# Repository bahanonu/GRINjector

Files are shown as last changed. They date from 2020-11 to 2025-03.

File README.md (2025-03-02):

# GRINjector

<!-- ![image](https://user-images.githubusercontent.com/5241605/97932336-945bbb80-1d24-11eb-9098-b09245b89beb.png) -->
<!-- ![image](https://user-images.githubusercontent.com/5241605/98111332-4a262780-1e55-11eb-887c-673c79a5a353.png) -->

<!-- <img src="https://user-images.githubusercontent.com/5241605/124192957-f23ecf80-da7a-11eb-9894-70a6294c9538.png" width="42%" align="right" alt="ciatah_logo"> -->






__GRINjector__ is a device for injecting gradient-refractive index (GRIN) lens probes into animals. The advantages are:
1. The injection needle displaces brain tissue, improving targetting and minimizing tissue compression.
2. The GRIN is held in place during retraction of the placement needle from the GRIN and the GRINJector device.
3. The guide needle can be easily swapped for other guide needles depending on the diameter and length of the GRIN lens probe.

This repository contains CAD files for printing GRINjector version 3.0 components and assembling them into a usable GRINjector. 

The assembly and use of the GRINjector is also detailed in our book chapter.
* GRINjection section: https://link.springer.com/protocol/10.1007/978-1-0716-2039-7_13#Sec6.
* Fig. 3: https://link.springer.com/protocol/10.1007/978-1-0716-2039-7_13/figures/3.

For those conducting calcium imaging experiments and analysis, we have a software package called CIAtah: https://github.com/bahanonu/ciatah.

Questions? Contact: Biafra Ahanonu (github [at] bahanonu [dot] com).

## Components

The below figure illustrates several of the main components:



Below is a list of components needed to assemble a GRINjector:
* Vernier micrometer. SM-13. Newport.
* Bearing stage. 9066-COM. Newport.
* 4x lock screws that come with 9066-COM.
* Model 1770, Kopf Instruments. For attaching GRINjector to stereotaxic arm.
* GRINjector bottom connector (`grinjector_bottom_connector`)
* GRINjector main needle connector top (`grinjector_mainneedle_connector_top`)
* GRINjector main needle connector bottom (`grinjector_mainneedle_connector_bottom`)
* Stereotaxic holder attachment (`stereotaxic_holder_attachment`)
* 2x - 8-32 x 1'' cap screw.
* 1x - 4-40 x 3/16'' cap screw.
* 1x - 4-40 x 1/4'' cap screw.
* 4x - 4-40 x 5/16'' cap screw.
* Luer lock needle (`Holder needle`) matched to the size of the GRIN lens probe.
  * For 1-mm GRIN lens probe, recommend 17G needle that is 0.04-0.042'' inner diameter (e.g. https://www.mcmaster.com/6710A24/).
    * Rubber tubing: https://www.mcmaster.com/5236K203/.
  * For 0.5-mm GRIN lens probe, recommend 21G needle (e.g. https://www.mcmaster.com/6710A28/).
* Thin needle (`Stability needle`) that is ~80-mm long and between 0.25-0.5-mm diameter (smaller version for smaller GRIN lens probes).
  * 0.25-mm diameter: https://www.mcmaster.com/6710A48/.
  * 0.5-mm diameter: https://www.mcmaster.com/6710A28/.
  * Used to hold the GRIN probe in place as outer sheath is removed. For the above pieces, may need to cut the metal piece from the Luer lock portion.

## Printing

The main parts are provided as STEP and STL files to allow printing on nearly all commonly used 3D printers (Straysys, uPrint, ). We recommend printing with a high-resolution printer to ensure optimal fit and one with easy to remove support material—we have used VeroBlackPlus on a Stratasys Objet30 and found that to work quite well.

## Assembly

Below are step-by-step by step instructions for assembling the GRINjector after building the necessary parts.

1. Connect the SM-13 and 9066-COM to form a functional setup. Remove the locking plate from 9066-COM as below (see https://www.newport.com/medias/sys_master/images/images/he5/h5b/9366526427166/906806B-9066-9067-User-Manual.pdf).



2. Using 8-32 cap screws, connect the `Stereotaxic holder attachment` to the back of the 9066-COM, connecting to the top-most holes near the micrometer.



3. Next, pull down the bearing stage so that the two 4-40 holes in the back are exposed, place 4-40 x 5/16'' cap screws in each hole.



4. Tap the `grinjector_mainneedle_connector_bottom` holes with a 4-40 tap then place it onto `9066-COM` as below and screw in the 4-40 x 5/16'' cap screws (red below).



5. Align the `lock screws` that comes with `9066-COM` to each of the four holes on each side of the `grinjector_bottom_connector`.



6. Next, place a blunt or syringe tip `Holder needle` that matches the size of your GRIN lens probe into the groove of the `grinjector_mainneedle_connector_bottom` piece then place the `grinjector_mainneedle_connector_top` piece on top. Screw the `grinjector_mainneedle_connector_top` in place with 4-40 x 5/16'' cap screws then secure the `Holder needle` with a 4-40 x 1/4'' cap screw.

  * Syringe tip Luer-lock needles allow easier parting of the underlying tissue as the GRINjector is lowered into the brain or spinal cord tissue.



7. Next, obtain a long, `Stability needle` (e.g. ~80-mm long, 0.5-mm diameter) and thread through the small opening at the top of `grinjector_bottom_connector`. The `Stability needle` will then go through the `Holder needle`. Lock the needle in place with a 4-40 x 3/16'' cap screw.

  * Note that the end of the `Stability needle` can be sanded or polished to avoid the chance that it will scratch the GRIN lens probe during implantation and retraction.



8. Lastly, verify that the chosen `Holder needle` fits the GRIN lens probe tightly and that you can push the GRIN lens probe out of the `Holder needle` smoothly by twisting the SM-13 micrometer.
  
  * Note: rubber tubing (e.g. for 1-mm diameter probes, https://www.mcmaster.com/5236K203/) can be placed at the end of the `Holder needle` to ensure the GRIN lens does not slip from the GRINjector during use while still allowing the `Holder needle` to be retracted from around the GRIN.



You are now done assembled the GRINjector! Happy imaging.



## Animal experiments

To use the GRINjector in an animal:
* Attach the GRINjector onto a stereotaxic arm then perform your normal GRIN lens probe crainotomy surgery.
* Lower the GRIN into the brain using the GRINjector (below diagram, left).
* After placement at desired coordinates in tissue, raise the blunt tip needle by twisting the micrometer until the needle is clear of the GRIN lens probe. The red needle secures the GRIN in place during retraction of the device.
* Secure the GRIN in place with dental cement, UV glue, or your adhesive of choice then after it as set, slowly raise the GRINjector using the stereotaxic arm.
* If your stereotaxic arm allows angles, the GRINjector can be used to target the same site at different angles to avoid vasculature or vital brain regions (below diagram, right).



## Head bar

We use several different headbar designs that allow us to clamp the animal during baseplate mounting, attaching the miniature microscope before experiments, and other uses. An example head bar design can be found in `cad_files/DXF`.



## Notes

`Holder needle`:
* SAI Infusion works well: https://www.sai-infusion.com/products/blunt-needles?variant=333055723. The plastic has some give that works well with the 3D printed parts.
* Check that the needle inner diameter is as close to the GRIN lens size as possible, e.g. for 1-mm that would be 17G needles that are ~0.04-0.042'' (https://www.mcmaster.com/6710A24/). 
* Sometimes users have to check a couple needles within the same batch since there will be slight size variations that will optimally fit their GRIN lenses.

`Stability needle`:
* We have found that a metal needle (e.g. could go with https://www.mcmaster.com/6710A48/ or similar then cut the needle to the desired length) does not cause significant scratching.
* If you have a grinder (handheld or bench), polisher (e.g. https://www.ultratecusa.com/product/ultrapol-end-edge-polisher/), or similar surface, then you can make the needle surface smoother and flat. 
* Alternatively can place a small drop of optical glue on the end of the needle and cure it or look for plastic needles.

## Acknowledgements

I would like to thank [Prof. Benjamin Grewe](https://www.ini.uzh.ch/en/institute/people?uname=bgrewe) for helping inspire and provide feedback on the initial GRINjector design.

## References

Please cite the [Ahanonu and Corder, 2022](https://doi.org/10.1007/978-1-0716-2039-7_13) book chapter if you used procedures detailed here.

```bibtex
@incollection{ahanonu2022recording,
  title={Recording Pain-Related Brain Activity in Behaving Animals Using Calcium Imaging and Miniature Microscopes},
  author={Ahanonu, Biafra and Corder, Gregory},
  booktitle={Contemporary Approaches to the Study of Pain},
  pages={217--276},
  year={2022},
  publisher={Springer}
}
```

Alternatively, please cite our publication [Corder*, Ahanonu*, et al. _Science_ 2019](http://science.sciencemag.org/content/363/6424/276.full) :

```Latex
@article{corderahanonu2019amygdalar,
  title={An amygdalar neural ensemble that encodes the unpleasantness of pain},
  author={Corder, Gregory and Ahanonu, Biafra and Grewe, Benjamin F and Wang, Dong and Schnitzer, Mark J and Scherrer, Gr{\'e}gory},
  journal={Science},
  volume={363},
  number={6424},
  pages={276--281},
  year={2019},
  publisher={American Association for the Advancement of Science}
}
```

## License

Copyright (C) 2015-2025 Biafra Ahanonu

This project is licensed under the terms of the MIT license. See LICENSE file for details.

## Repository stats
- Hits (starting 2020.11.02)
-  (starting 2020.11.02)

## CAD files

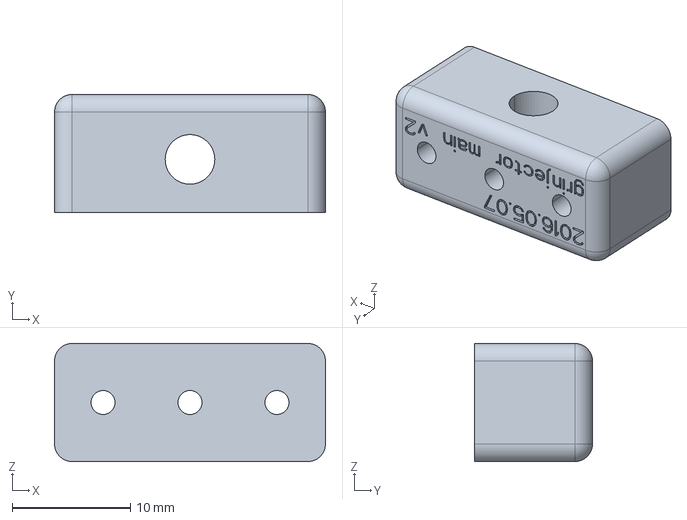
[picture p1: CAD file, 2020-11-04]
cad_files/STEP/grinjector_mainneedle_connector.stp
22.9 x 10.0 x 10.0 mm

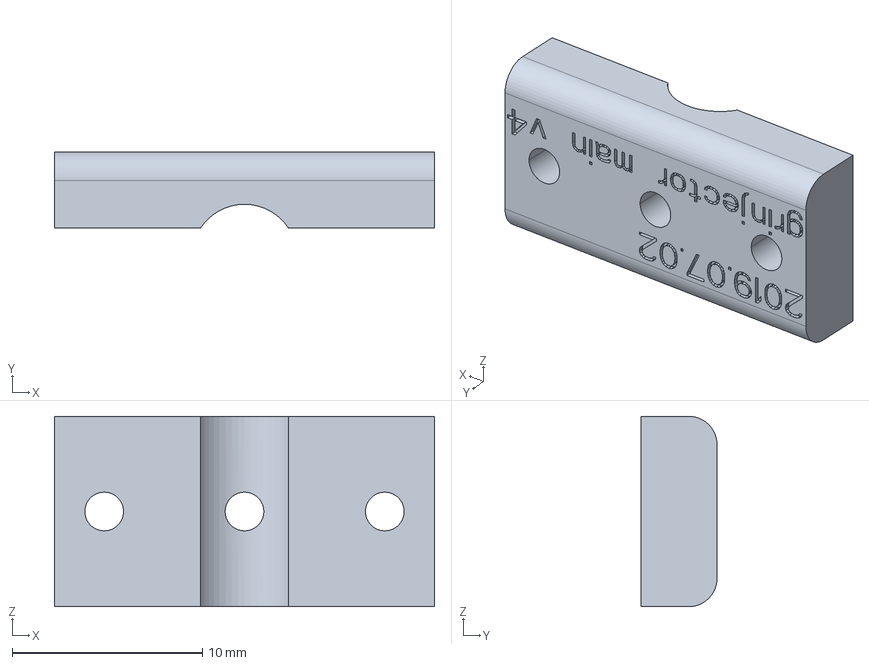
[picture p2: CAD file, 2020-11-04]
cad_files/STEP/grinjector_mainneedle_connector_top.stp
19.9 x 4.00 x 10.0 mm

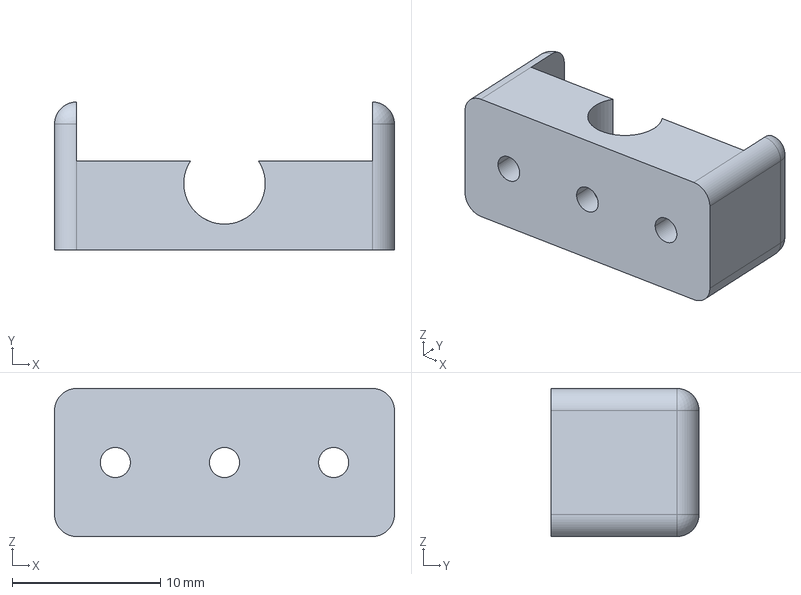
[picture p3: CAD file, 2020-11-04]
cad_files/STEP/grinjector_mainneedle_connector_bottom.stp
22.9 x 10.0 x 10.0 mm

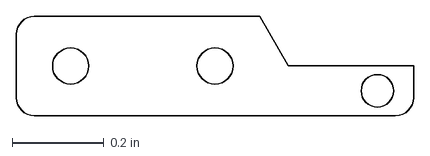
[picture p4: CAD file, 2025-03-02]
cad_files/DXF/headbar.dxf
0.866 x 0.217 in

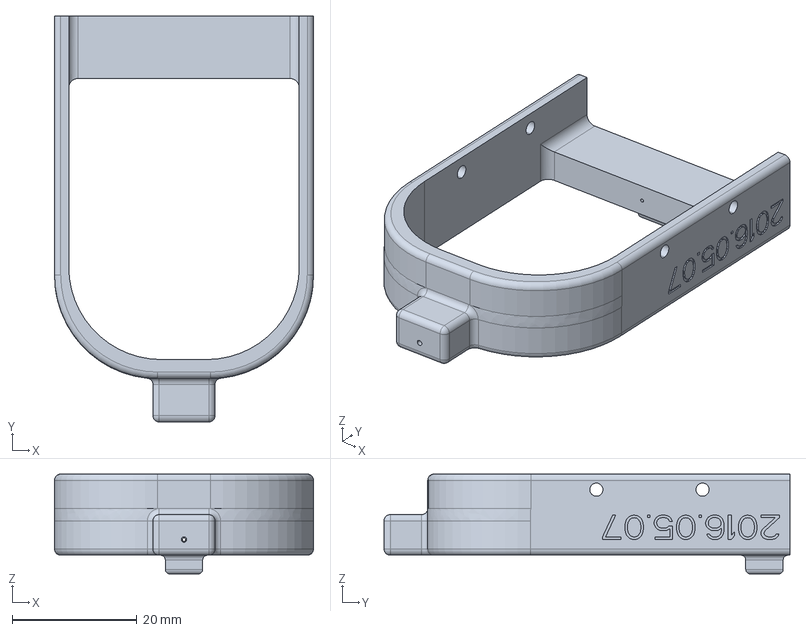
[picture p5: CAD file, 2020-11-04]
cad_files/STEP/grinjector_bottom_connector.stp
41.5 x 65.0 x 16.0 mm

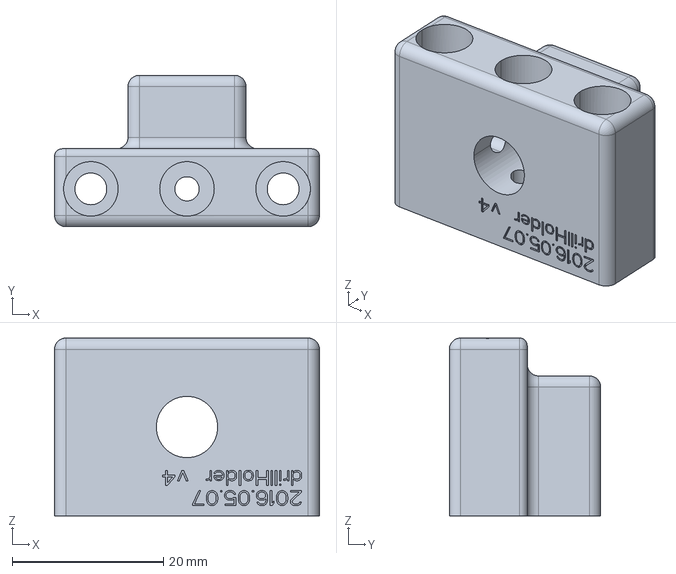
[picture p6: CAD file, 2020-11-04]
cad_files/STEP/stereotaxic_holder_attachment.stp
35.0 x 20.0 x 23.5 mm

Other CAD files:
cad_files/STL/grinjector_bottom_connector.stl
cad_files/STL/grinjector_mainneedle_connector.stl
cad_files/STL/grinjector_mainneedle_connector_bottom.stl
cad_files/STL/grinjector_mainneedle_connector_top.stl
cad_files/STL/stereotaxic_holder_attachment.stl

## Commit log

2020-11-04 Add CAD files and update README
    [grinjector_bottom_connector.stl, grinjector_bottom_connector.stp, grinjector_mainneedle_connector.stl, grinjector_mainneedle_connector.stp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]
2025-03-02 Update README and add headbar DXF
    [headbar.dxf]
